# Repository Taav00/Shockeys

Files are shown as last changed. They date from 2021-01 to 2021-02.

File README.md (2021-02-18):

# Check-y

This project was completed as part of the Chinese Hardware Innovation Camp (CHIC) program, a Master's minor at the Swiss Federal Institute of Technologly in Lausanne (EPFL), Switzerland.

## Table of Contents

* [Description](#description)
* [App screenshots](#app-screenshots)
* [Tech/frameworks used](#techframeworks-used)
* [Hardware needed](#hardware-needed)
* [Setup](#setup)
* [How to use our device](#how-to-use-our-device)
* [Sources](#sources)
* [Authors](#authors)
* [License](#license)

## Description 

The main goal of this device is to **detect large head impacts** **sustained by athletes**. An **alert** is displayed by the **app** when the acceleration is considered dangerous and may require an examination of the player.

The project can be broken down into **4 modules**. The features detailed in the schematic below have all been successfully implemented.

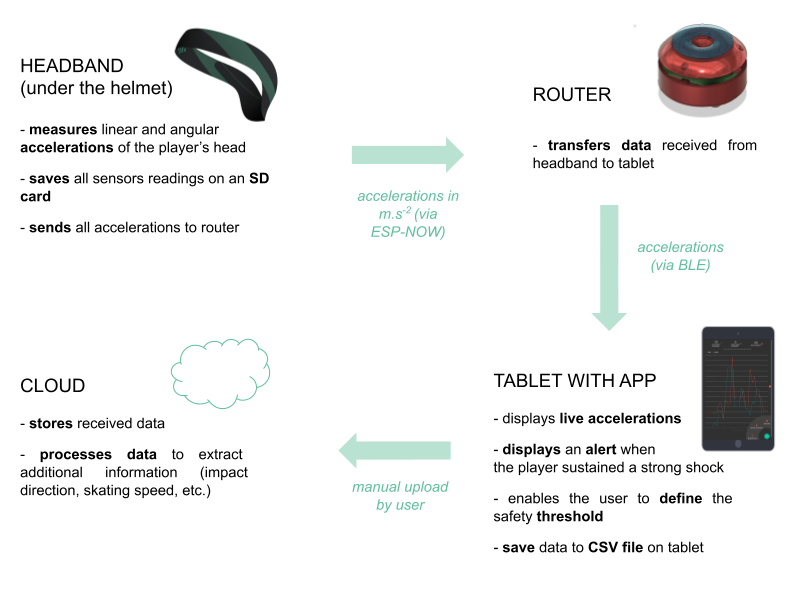
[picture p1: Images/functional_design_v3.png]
features


## App screenshots

Through the app, the user can:

- [x] **connect** to the router (via BlueTooth)
- [x] receive data from a headband (via the router)
- [x] read **live linear & angular accelerations** 
- [x] plot these accelerations during a chosen time period
- [x] define his / her **safety threshold**
- [x] receive an **alert** when the acceleration exceeds the defined threshold
- [x] **download** the received **data** as a CSV file

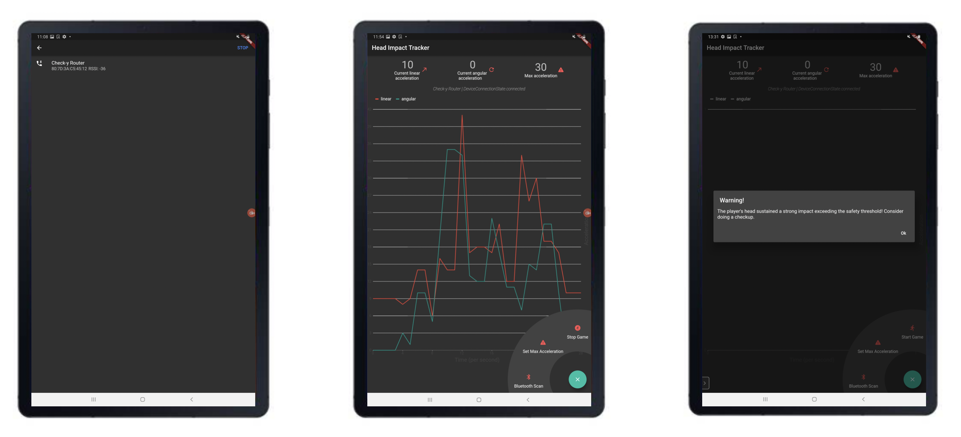
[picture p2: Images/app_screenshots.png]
screenshots


## Tech/frameworks used

To develop this product, we used:

- the [Arduino](https://www.arduino.cc/) IDE to code the firmware in **C++**
- the [Flutter](https://flutter.dev/?gclid=Cj0KCQiAvbiBBhD-ARIsAGM48bxFAGzs3gWAGN6dBFMqM3unjVbl-PyLLc8HqQ3UjYQjHzmKjB7pjHkaAgyKEALw_wcB&gclsrc=aw.ds) framework to develop a cross-platform app
- [EasyEDA](https://easyeda.com/fr) to design our custom PCB for the headband
- [Django](https://www.djangoproject.com/) and **Python** to build our mySQL database and [Bootstrap](https://getbootstrap.com/) for the database frontend
- [Google Cloud](https://cloud.google.com/) to migrate ou database online 

## Hardware needed

- an **ESP32** board (e.g., a DO IT ESP32 DEVKIT V1 board) for the router
- our **custom PCB** for the headband (cf. the "Hardware" folder )
- a **tablet** or smartphone to run the Flutter app (⚠️ the app has only been tested on Android)

## Setup

In order to execute and upload properly the firmware to a router or a headband, you must first
make sure that the Arduino IDE has been correctly setup:

1. install the [Arduino IDE](https://www.arduino.cc/en/software)
2. install the **ESP32 board module** ([procedure](https://randomnerdtutorials.com/installing-the-esp32-board-in-arduino-ide-windows-instructions/))
3. for the router, choose Tools > Board > ESP32 Arduino > WEMOS LOLIN32 (important
   to be able to change the “Partition Scheme” (also in Tools) to “No OTA (Large APP)”
4. for the router, choose Tools > Board > ESP32 Arduino > DO IT ESP32 DEVKIT V1
5. ⚠️ add our two **custom libraries** (Adafruit LIS331 & Bolder Flight Systems BMI088 in the Firmware > "Custom Libraries" folder) using Arduino > Sketch > Include Library > Add .ZIP Library
6. add the “Adafruit BusIO” and “Adafruit Unified Sensor” libraries using Arduino > Tools > Manage Libraries

Once the Arduino IDE is correctly setup:

1. load the **headband firmware** onto our **custom PCB**
2. place the PCB inside the headband
3. load the **router firmware** onto an **ESP32 board** (we used a DO IT ESP32 DEVKIT V1 board)
4. download the **app** on a **tablet** / smartphone

## How to use our device 

To send the measured accelerations from the headband to the tablet:

1. **turn on** the **router** (press the button once)
2. wait a second
3. **turn on** the headband (using the switch)
4. open the app on the tablet
5. click on the expandable menu at the bottom right of the app
6. click on "**Bluetooth scan**"
7. a new window should have opened displaying the detected BLE devices → select "**Check-y router**"

After approximately 7 seconds, the live accelerations should be displayed on the app.

## Sources 

We used Chase Strickler's hear rate app ([GitHub](https://github.com/strcklr/DDish-Coding-Challenge/tree/5ae8deb23e88ea74f1a3f7b782157082140903fa/heartrateapp)) as a starting point for our own app. 

## Authors

🧑🏻‍🏭 **Taavet Kangur** (in charge of the hardware development) <br>
👩🏼‍💻 **Diane Marquette** (in charge of the firmware and app development) <br>
🧑🏾‍💻 **Maëlick Brochut** (in charge of the signal processing and back-end) <br>
👩🏻‍🎨 **Marine Fondin** (in charge of the headband design) <br>
💵 **Nicolas Mauroux** (the business guy)

## License

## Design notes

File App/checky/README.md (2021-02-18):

# Check-y

A new Flutter application.

## Getting Started

This project is a starting point for a Flutter application.

A few resources to get you started if this is your first Flutter project:

- [Lab: Write your first Flutter app](https://flutter.dev/docs/get-started/codelab)
- [Cookbook: Useful Flutter samples](https://flutter.dev/docs/cookbook)

For help getting started with Flutter, view our
[online documentation](https://flutter.dev/docs), which offers tutorials,
samples, guidance on mobile development, and a full API reference.

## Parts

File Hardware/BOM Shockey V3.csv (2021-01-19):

ID | Name | Designator | Footprint | Quantity | Manufacturer Part | Manufacturer | Supplier | Supplier Part | LCSC Assembly | JLCPCB SMD
1 | 4.7K | R16,R14 | R0603 | 2 | 0603WAF4701T5E | UniOhm | LCSC | C23162 | Yes
2 | IPTG14K-V-T/R | SW3 | SW-SMD_IPTG1 | 1 | IPTG14K-V-T/R | Diptronics | LCSC | C240297
3 | DMG2307L-7 | Q1 | SOT-23-3_L2.9-W1.6-P1.90-LS2.8-BR | 1 | DMG2307L-7 | DIODES | LCSC | C102620 | Yes
4 | 10uF | C2 | C0603 | 1 | CL10A106KP8NNNC | SAMSUNG | LCSC | C19702 | Yes
5 | 4.7uF | C10,C11 | C0603 | 2 | CL10A475KO8NNNC | SAMSUNG | LCSC | C19666 | Yes
6 | BMI088 | U3,U5 | LGA-16-L4.5-W3.0-P0.50_TL | 2 | BMI088 | Bosch Sensortec | LCSC | C194919 | Yes
7 | 100K | R9,R10,R11 | R0603 | 3 | RTT03104JTP | RALEC | LCSC | C103211
8 | SM02B-SRSS-TB (LF)(SN) | CN1 | CONN-SMD_2P-P1.00_SM02B-SRSS-TB(LF)(SN) | 1 | - | JST Sales America | LCSC | C160402
9 | SS-1300B | SW4 | SW-SMD_SS-1300B | 1 | SS-1300B | RI SHENG | LCSC | C589302
10 | BAT20JFILM | D1 | SOD-323_L1.8-W1.3-LS2.5-RD | 1 | BAT20JFILM | STMicroelectronics | LCSC | C155590 | Yes
11 | 100nF | C1,C6,C9,C3,C13,C7,C17,C14,C16 | C0603 | 9 | CC0603KRX7R9BB104 | YAGEO | LCSC | C14663 | Yes
12 | 19-217/GHC-YR1S2/3T | LED4,LED1 | LED0603-R-RD | 2 | 19-217/GHC-YR1S2/3T | EVERLIGHT | LCSC | C72043 | Yes
13 | 10nF | C19,C15,C8,C12,C18 | C0603 | 5 | 0603B103J500NT | FH | LCSC | C124567
14 | PAD | U4 | PAD-60-31-RECT | 1
15 | TS-1057S-03126 | SW1 | SW-SMD_4P-L6.0-W6.0-P4.50-LS11.0 | 1 | TS-1057S-03126 | XUNPU | LCSC | C455256
16 | WS2812B-MINI | LED3 | LED-SMD_4P-L3.5-W3.5-TL_WS2812B | 1 | WS2812B-Mini | Worldsemi | LCSC | C527089 |  | Yes
17 | H3LIS331DL | U1,U7 | LGA16-0.5-3X3MM | 2 | H3LIS331DL
18 | 1K | R1,R2,R8,R15,R7,R6 | R0603 | 6 | 0603WAF1001T5E | UniOhm | LCSC | C21190 |  | Yes
19 | MCP73831T-2ATI/OT | CHARGER1 | SOT-23-5_L3.0-W1.7-P0.95-LS2.8-BL | 1 | MCP73831T-2ATI/OT | MICROCHIP | LCSC | C14879 | Yes
20 | 10K | R20,R23,R24,R19,R12,R13,R17,R18,R5 | R0603 | 9 | RMC060310K1%N | Tyohm | LCSC | C269701
21 | FT232RL-REEL | U6 | SSOP-28_L10.2-W5.3-P0.65-LS7.8-BL | 1 | FT232RL-REEL | FTDI | LCSC | C8690 | Yes
22 | SS8050_C109068 | Q2,Q3 | SOT-323-3_L2.2-W1.3-P1.30-LS2.1-BR | 2 | SS8050 | CJ | LCSC | C109068 | Yes
23 | 56pF | C4,C5 | C0603 | 2 | 0603CG560J201NT | FH | LCSC | C63689
24 | R27 | R4,R3 | R0603 | 2 | 0603WAF270JT5E | UniOhm | LCSC | C25190 | Yes
25 | U-F-M5DD-Y-L1 | USB2 | MICRO-USB-SMD_MICRO-USB-A8 | 1 | U-F-M5DD-Y-L1 | HRO | LCSC | C145791
26 | AP2112K-3.3TRG1 | POWER_REG1 | SOT-25-5_L3.0-W1.8-P0.95-LS3.0-BL | 1 | AP2112K-3.3TRG1 | DIODES | LCSC | C51118 | Yes
27 | ESP-WROOM-32 | U2 | WIFIM-SMD_ESP-WROOM-32 | 1 | ESP-WROOM-32 | ESPRESSIF | LCSC | C95209
28 | TF-115 | CARD1 | TF-SMD_TF-115 | 1 | TF-115 | XUNPU | LCSC | C266620

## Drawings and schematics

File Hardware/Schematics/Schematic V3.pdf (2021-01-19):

# IO12 14 GND 15

IO0 25 IO4 26 IO16 27 IO17 28 IO5 29 IO18 30 IO19 31 NC 32 IO21 33 RXD0 34 TXD0 35 IO22 36 IO23 37 GND 38

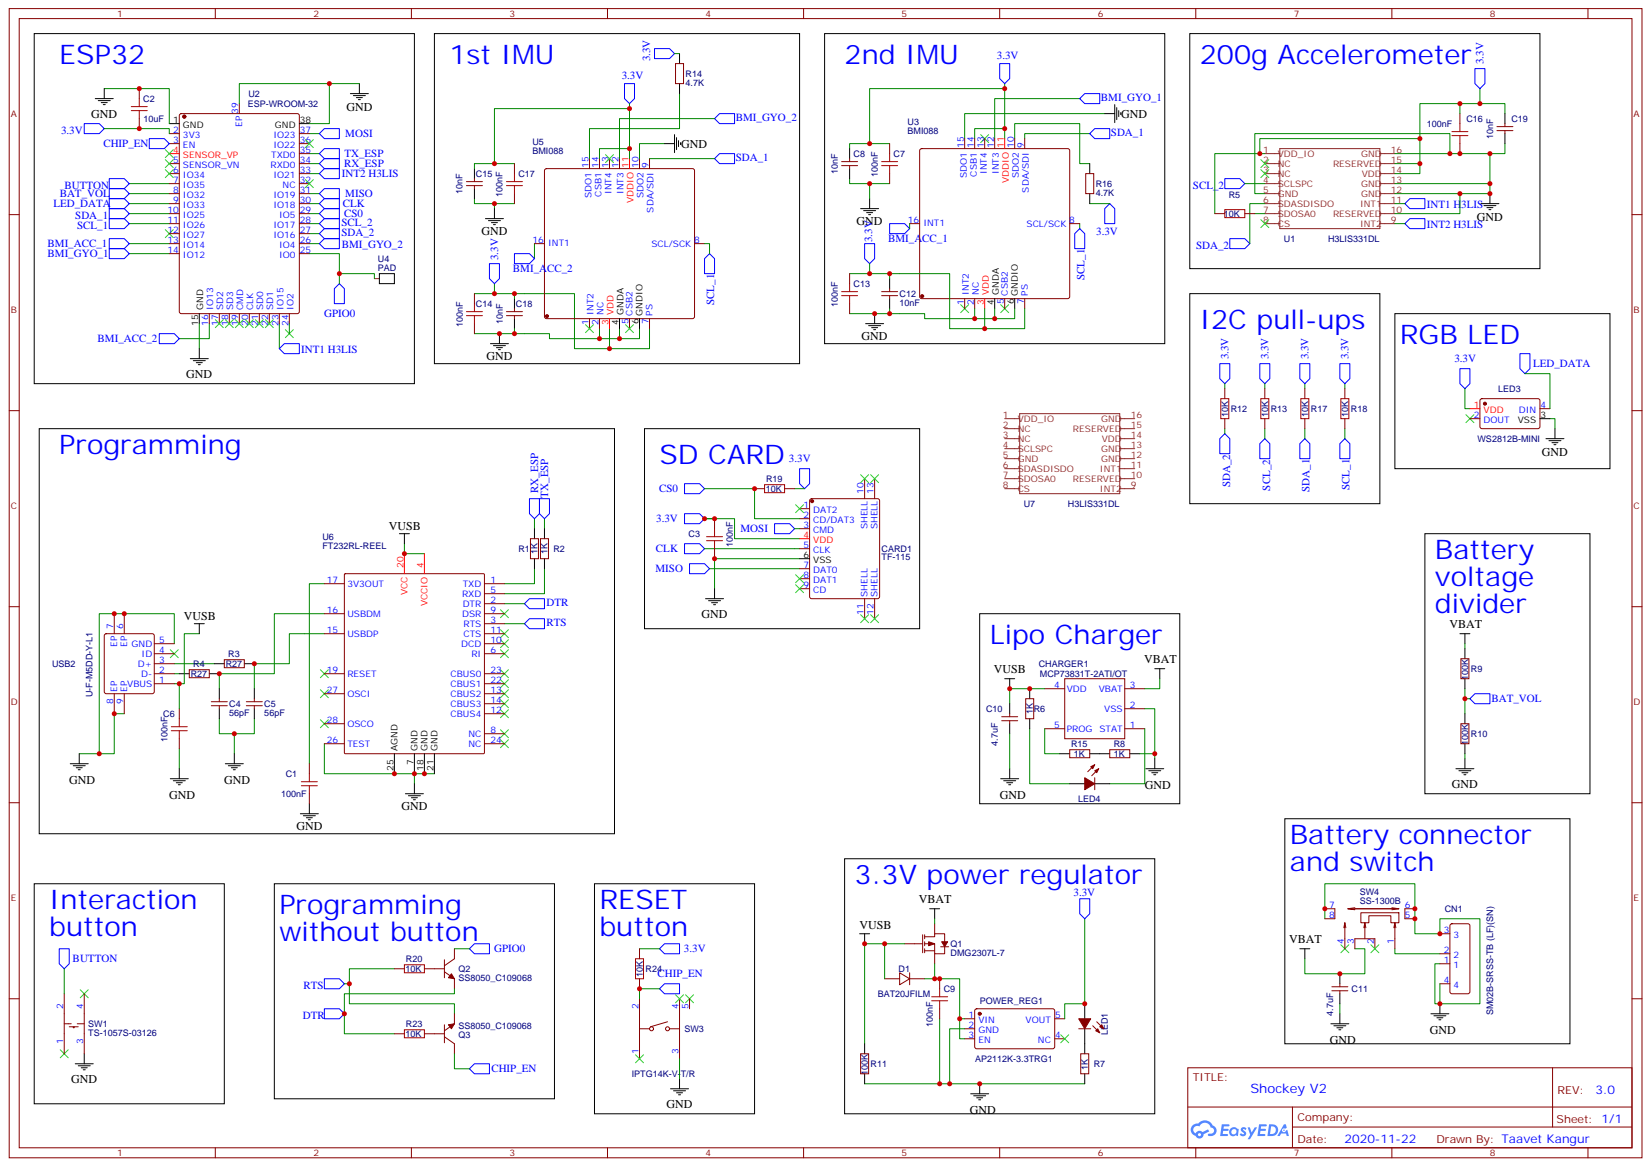
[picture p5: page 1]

7 SCL/SCK 8 SDA/SDI

SM02B-SRSS-TB (LF)(SN)

Drawn By: Taavet Kangur

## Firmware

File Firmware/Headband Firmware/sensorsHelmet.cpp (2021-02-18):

/*

Author: Diane Marquette
Last modification: January 2021 
  
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
Definition: Implements all functions, variables and constants needed by
sensors.
*/

#include "sensorsHelmet.h"
#include <Wire.h>
#include <Adafruit_Sensor.h>


// Bus addresses for sensors
#define ADD_ACC_1       0x18
#define ADD_ACC_2       0x19
#define ADD_ACC_3       0x19 // same as ADD_ACC_2 but on a different I2C bus
#define ADD_GYRO_1      0x68
#define ADD_GYRO_2      0x69

// 1st I2C bus -> for IMUs
#define I2C_1_SDA       25
#define I2C_1_SCL       26

// 2nd I2C bus -> for big accelerometer
#define I2C_2_SDA       16
#define I2C_2_SCL       17

#define I2C_FREQ        400000

#define H3LIS_RANGE     H3LIS331_RANGE_100_G       
#define LIS_DATARATE    LIS331_DATARATE_1000_HZ

TwoWire I2Cone = TwoWire(1);
TwoWire I2Ctwo = TwoWire(2);


/* Accelerometers of IMUs */ 
Bmi088Accel accel_1(I2Cone,ADD_ACC_1);
Bmi088Accel accel_2(I2Cone,ADD_ACC_2);

/* Gyroscopes of IMUs */
Bmi088Gyro gyro_1(I2Cone,ADD_GYRO_1);
Bmi088Gyro gyro_2(I2Cone,ADD_GYRO_2);

/* Accelerometer for large impacts */ 
Adafruit_H3LIS331 lis = Adafruit_H3LIS331();

/* Structure to store the most recent event from sensor LIS*/
sensors_event_t event;


/* Function starting all 3 sensors and the required I2C buses*/
void setup_sensors(){

  int status;
  
  // setup I2C buses
  I2Cone.begin(I2C_1_SDA,   I2C_1_SCL,  I2C_FREQ);
  delay(50);
  I2Ctwo.begin(I2C_2_SDA,   I2C_2_SCL,  I2C_FREQ);
  delay(50);

  // start big accelerometer
  if (! lis.begin_I2C(ADD_ACC_3, &I2Ctwo)) {   
    Serial.println("Couldnt start H3LIS");
    while (1) yield();
  }
  delay(50);
  lis.setRange(H3LIS_RANGE);   
  lis.setDataRate(LIS_DATARATE);

  while(!Serial) {}
  
  // start IMU sensors
  status = accel_1.begin();
  if (status < 0) {
  // if (false) {
    Serial.println("Accel Initialization Error : Accel 1");
    Serial.println(status);
    while (1) {}
  }
  status = accel_2.begin();
  if (status < 0) {
    Serial.println("Accel Initialization Error : Accel 2");
    Serial.println(status);
    while (1) {}
  }
  
  status = gyro_1.begin();
  if (status < 0) {
  // if (false) {
    Serial.println("Gyro Initialization Error : Gyro 1");
    Serial.println(status);
    while (1) {}
  }
  status = gyro_2.begin();
  if (status < 0) {
    Serial.println("Gyro Initialization Error : Gyro 2");
    Serial.println(status);
    while (1) {}
  }
}


/* Function reading data from all 3 sensors */
void read_sensors(){
  
  // read the IMUs linear accelerations 
  accel_1.readSensor();
  accel_2.readSensor();
  
  // read the IMUs angular accelerations
  gyro_1.readSensor();
  gyro_2.readSensor();
  
  // read linear accelerations from 200g accelerometer
  lis.read();      // get X Y and Z data at once
  // or....get a new sensor event, normalized
  lis.getEvent(&event);

}

/* Function returning acceleration along the x-axis according to the big accelerometer */
int16_t getBigAccX(){
  return event.acceleration.x;
}

/* Function returning acceleration along the y-axis according to the big accelerometer */
int16_t getBigAccY(){
  return event.acceleration.y;
}

/* Function returning acceleration along the z-axis according to the big accelerometer */
int16_t getBigAccZ(){
  return event.acceleration.z;
}


/* Function printing linear acceleration from IMUs in m/s^2 */
void print_accel(Bmi088Accel accel, int accelNb){
  Serial.printf("Accel_X_%d: %f /t", accelNb, accel.getAccelX_mss());
  Serial.printf("Accel_Y_%d: %f /t", accelNb, accel.getAccelY_mss());
  Serial.printf("Accel_Z_%d: %f /n", accelNb, accel.getAccelZ_mss());
}

/* Function printing angular acceleration from IMUs in rad/s */
void print_gyro(Bmi088Gyro gyro, int gyroNb){
  Serial.printf("Gyro_X_%d: %f /t", gyroNb, gyro.getGyroX_rads());
  Serial.printf("Gyro_Y_%d: %f /t", gyroNb, gyro.getGyroY_rads());
  Serial.printf("Gyro_Z_%d: %f /n", gyroNb, gyro.getGyroZ_rads());
}

/* Function printing linear acceleration from big accelerometer */
void print_big_accel(){
  // Display results as m/s^2 in a plot-friendly format
  Serial.printf("Accel_X_3 : %f /t", event.acceleration.x);
  Serial.printf("Accel_Y_3 : %f /t", event.acceleration.y);
  Serial.printf("Accel_Z_3 : %f /n", event.acceleration.z);
}

/* Function copying sensor readings in message structure*/
struct_message copy_readings(struct_message readings){
   
   readings.IMU1_accX = accel_1.getAccelX_mss();
   readings.IMU1_accY = accel_1.getAccelY_mss();
   readings.IMU1_accZ = accel_1.getAccelZ_mss();
   readings.IMU1_gyrX = gyro_1.getGyroX_rads();
   readings.IMU1_gyrY = gyro_1.getGyroY_rads();
   readings.IMU1_gyrZ = gyro_1.getGyroZ_rads();

   readings.IMU2_accX = accel_2.getAccelX_mss();
   readings.IMU2_accY = accel_2.getAccelY_mss();
   readings.IMU2_accZ = accel_2.getAccelZ_mss();
   readings.IMU2_gyrX = gyro_2.getGyroX_rads();
   readings.IMU2_gyrY = gyro_2.getGyroY_rads();
   readings.IMU2_gyrZ = gyro_2.getGyroZ_rads();

   readings.LIS_accX = event.acceleration.x;
   readings.LIS_accY = event.acceleration.y;
   readings.LIS_accZ = event.acceleration.z;

   return readings;
}

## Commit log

2020-03-02 Add files via upload
    Sensors values from two IMUs. First value is time of microcontroller, then 3 acceletrations, 3 gyro and 3 acceletration from other IMU
    [Resting_Data.csv]
2020-03-04 Working ESP32 logging two IMU data into SD card
    Problem: when moved a little the logging stops.
2020-03-19 Add files via upload
    Code to send the data measured by the device under the helmet to the router next to the ice rink using ESP-NOW
2020-03-19 Code sending the data measured by the device under the helmet to the router using ESP-NOW
2021-01-19 Adding Hardware elements
    [BOM Shockey V3.csv, Gerber_BoardOutline.GKO, Gerber_BottomLayer.GBL, Gerber_BottomSilkLayer.GBO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]
